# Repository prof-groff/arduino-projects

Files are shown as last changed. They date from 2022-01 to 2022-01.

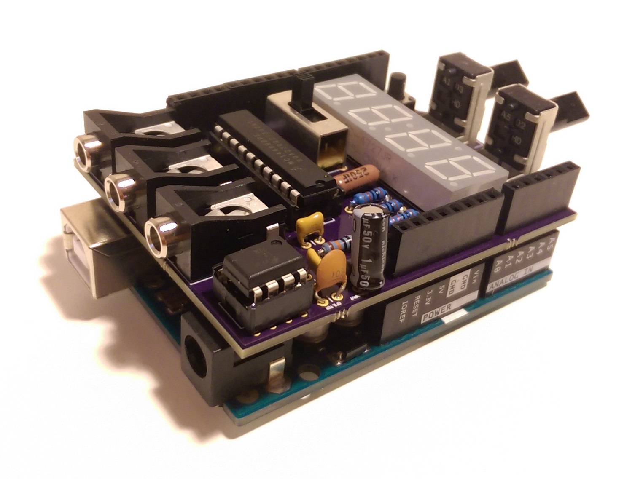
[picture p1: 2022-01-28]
WaveformsIO/img/AssembledBoard.jpg

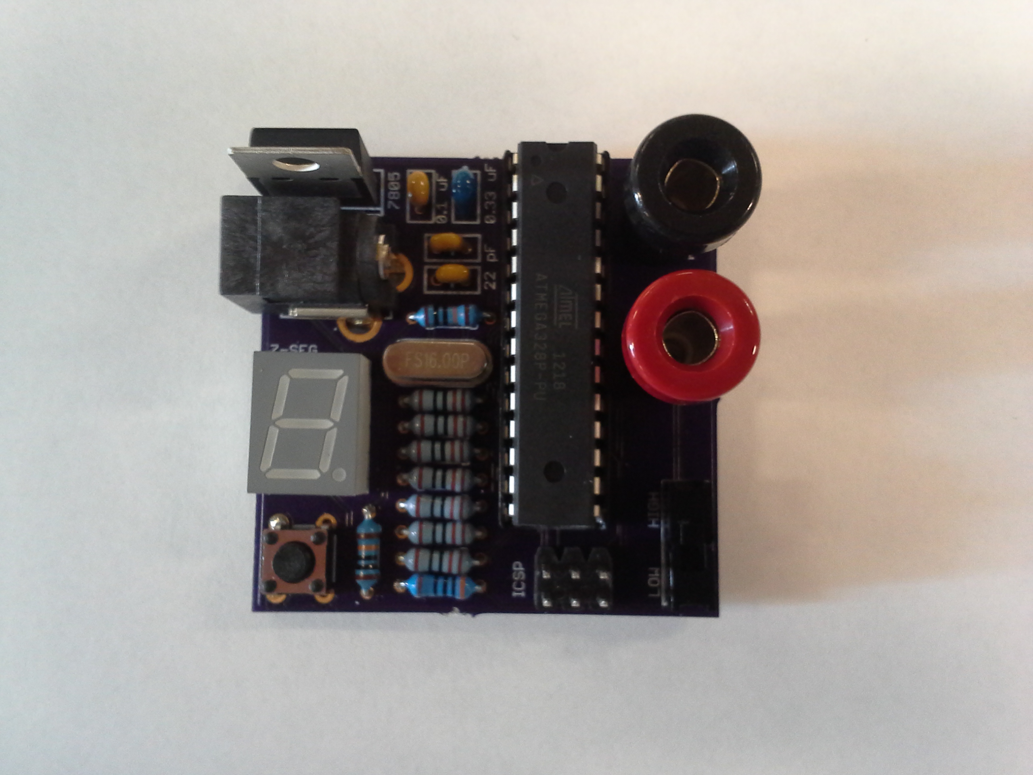
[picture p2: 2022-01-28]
makeToneBoard/img/toneMaker_assembled.jpg

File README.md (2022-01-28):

# arduino-projects

### makeToneBoard Parts List

* 1 x 28-pin DIP Atmel ATmega328p Microcontroller
* 1 x 28-pin DIP socket
* 1 x 7805 5-V linear voltage regulator
* 1 x Lite-On 4301-package 7-segment display
* 1 x 16 MHz Crystal
* 1 x SPST tactile switch/button, normally open, momentarily closed
* 1 x SPDT slide switch
* 1 x 2 rows, 6 positions header
* 1 x female 2.1 mm barrel jack
* 1 x black female banana plug jack
* 1 x red female banana plug jack
* 1 x 300 ohm resistor, 0.25W
* 7 x 110 ohm resistor, 0.25W
* 2 x 100 kohm resistor, 0.25W
* 2 x 22 pF ceramic capacitor, 100V
* 1 x 0.1 microF ceramic capacitor, 50V
* 1 x 0.33 microF ceramic capacitor, 50V

### WaveFormIO Parts List

* Motorola/Freescale MC14489B
* Lite-On LTC-4727JR 4-Digit Display
* ATmega 328P-PU
* 7805
* PTV09A-2020F-A502 Bourns 5k Poteniometer
* PTV09A-2020F-A103 Bourns 10k Poteniometer
* Push Button - Momentary On - Schurter 1301.9305
* E-Switch EG2301A (6mm-tall switch arm)
* 108-0903-001 (Black)
* 108-0902-001 (Red)
* Op-Amp for voltage follower
* TE Connectivity 1-971111-3 Flat Cable 10C 28AWG
* 3365/10-CUT-LENGTH 3M
* OMRON XG4M-1030-T Cable Crip Connector Female
* OMRON XG4C-1031 PCB Socket Male

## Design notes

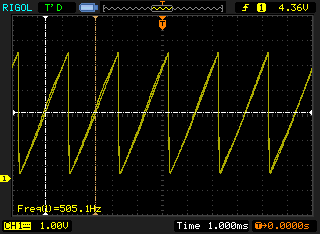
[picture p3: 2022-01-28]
WaveformsIO/img/sawtoothWave.bmp

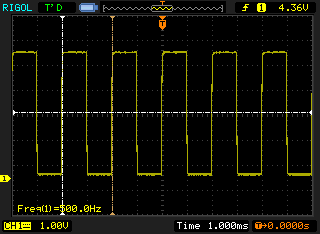
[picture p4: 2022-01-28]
WaveformsIO/img/squareWave.bmp

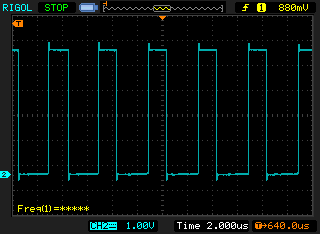
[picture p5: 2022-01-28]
WaveformsIO/img/PWM1.bmp

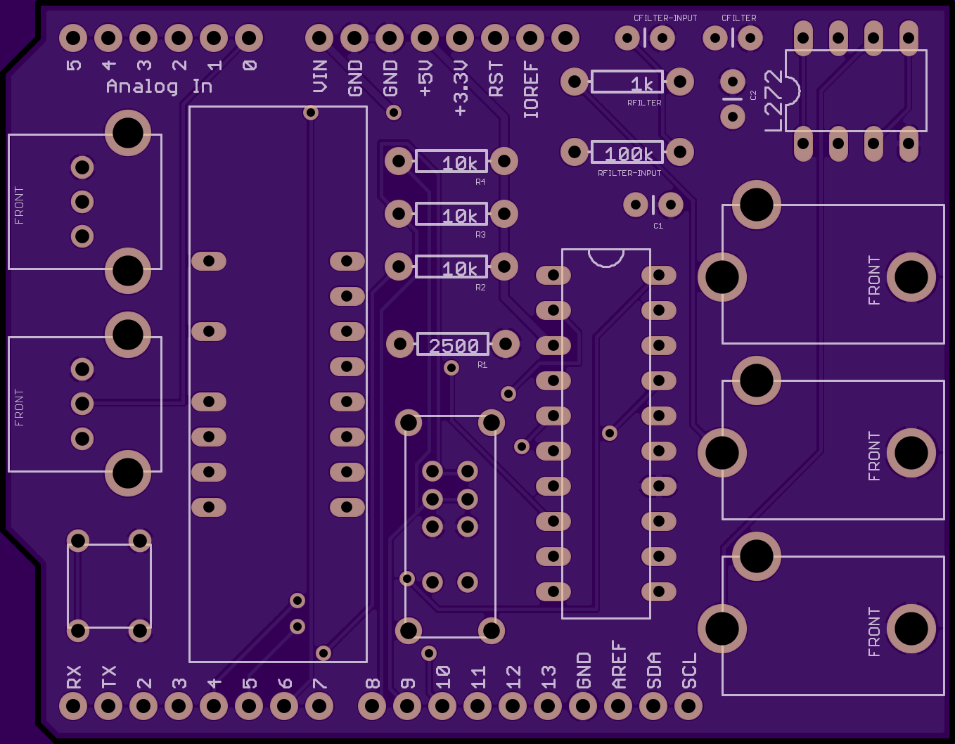
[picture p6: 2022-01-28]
WaveformsIO/img/OSHParkBoard.png

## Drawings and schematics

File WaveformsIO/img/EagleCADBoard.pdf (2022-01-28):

# Analog In RXTX

## CFILTER L272 CFILTER-INPUT C² C1

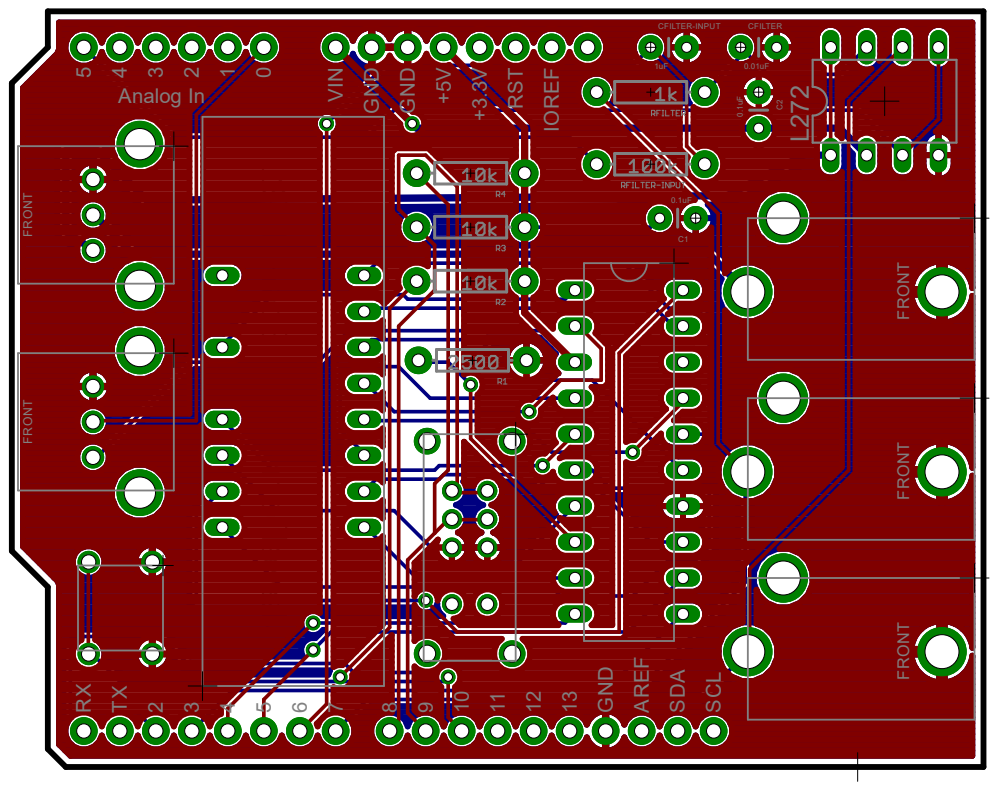
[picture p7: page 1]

910111213GND AREF SDA SCL IOREF FRONT FRONT FRONT FRONT FRONT

GND GND +5V RST VIN +3.3V5

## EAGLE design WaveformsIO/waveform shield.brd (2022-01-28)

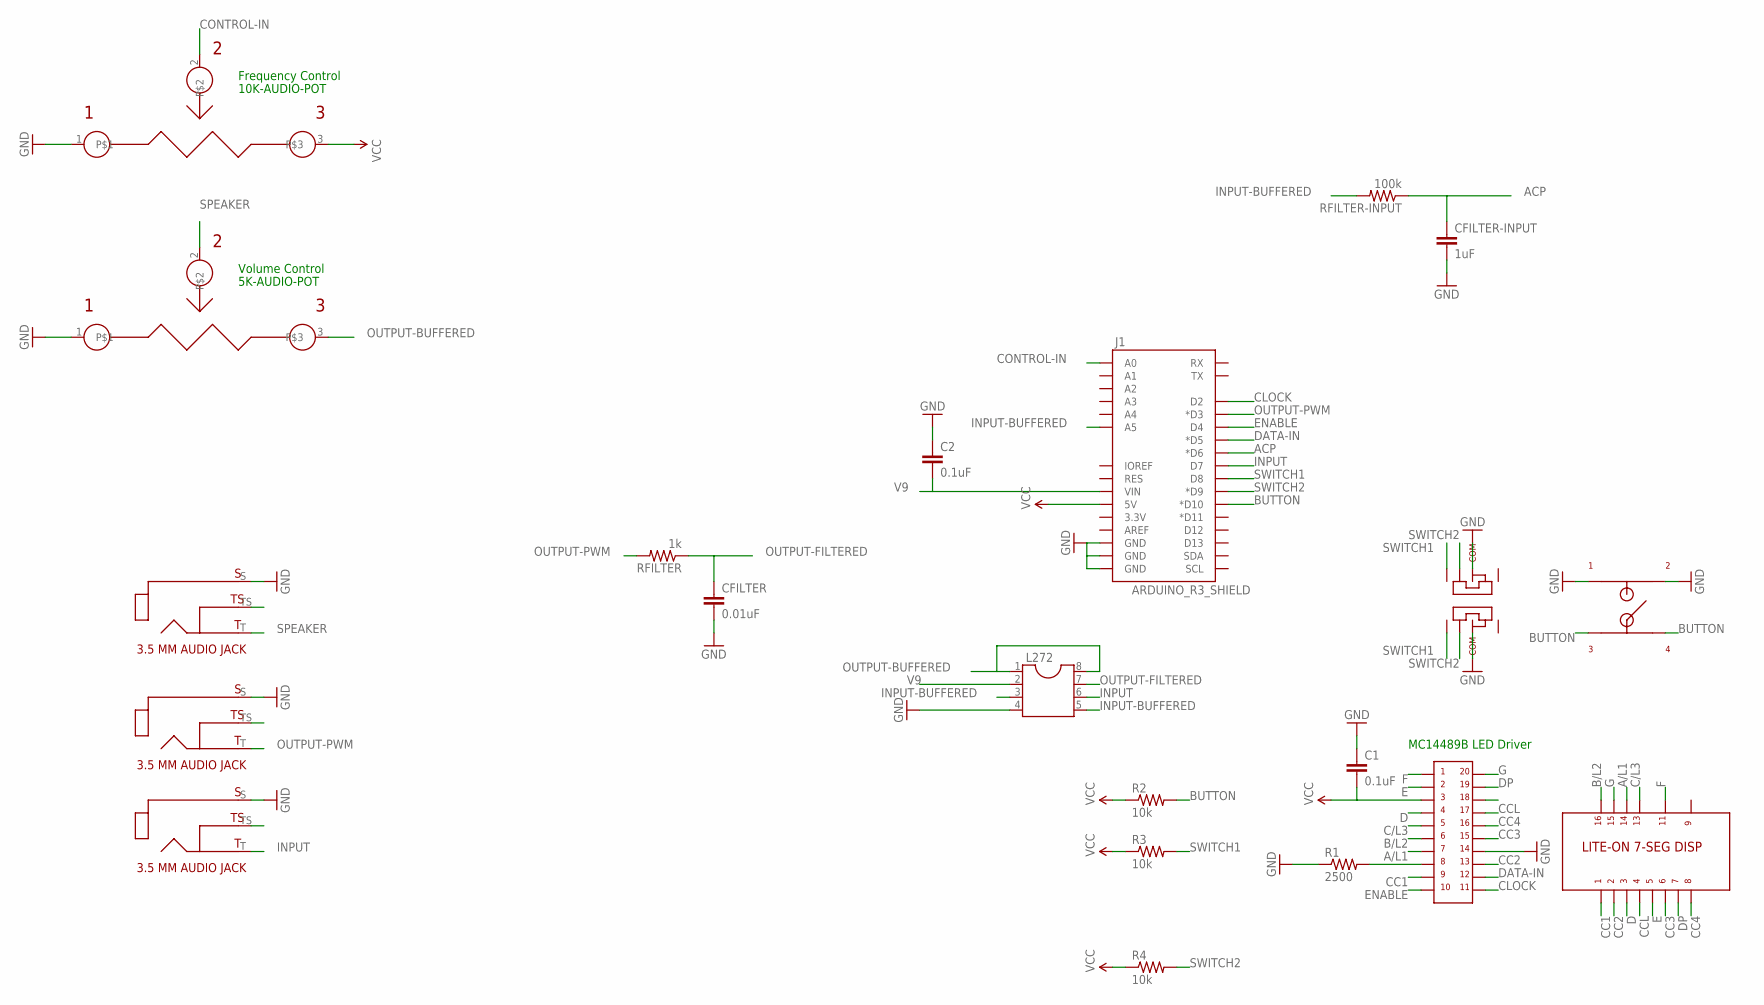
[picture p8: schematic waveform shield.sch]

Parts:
5K-AUDIO-POT: BOURNS-PTV09A-2; BOURNS-POT-PTV09A-2
C1, C2: 0.1uF; CAP-PTH-SMALL
CFILTER: 0.01uF; CAP-PTH-SMALL
CFILTER-INPUT: 1uF; CAP-PTH-SMALL
J1: ARDUINO_R3_SHIELD; UNO_R3_SHIELD
L272: DIL8; DIL08
R1: 2500; AXIAL-0.3
R2, R3, R4: 10k; AXIAL-0.3
RFILTER: 1k; AXIAL-0.3
RFILTER-INPUT: 100k; AXIAL-0.3
U$1: LITE-ON-7-SEG-DISP; 7-SEG-DISPLAY-LITE-ON
U$2: MC14489B-LED-DRIVER; DIP-20
U$3, U$6, U$7: 3.5MM-AUDIO-JACK-CUI; 3.5MM-AUDIO-JACK-MONO-CUI
U$4: E-SWITCH-THREE-WAY-SWITCH; EG2301-SLIDE-SWITCH
U$5: SWITCH-MOMENTARY-ON-SCHURTER
U$9: BOURNS-PTV09A-2; BOURNS-POT-PTV09A-2

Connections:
A/L1: U$1.P$14, U$2.P$7
ACP: CFILTER-INPUT.1, J1.D6 (*D6), RFILTER-INPUT.P$1 (1)
B/L2: U$1.P$16, U$2.P$6
BUTTON: J1.D10 (*D10), R2.P$2 (2), U$5.P$3, U$5.P$4
C/L3: U$1.P$13, U$2.P$5
CC1: U$1.P$1, U$2.P$9
CC2: U$1.P$2, U$2.P$13
CC3: U$1.P$6, U$2.P$15
CC4: U$1.P$8, U$2.P$16
CCL: U$1.P$4, U$2.P$17
CLOCK: J1.D2, U$2.P$11
CONTROL-IN: J1.A0, U$9.2
D: U$1.P$3, U$2.P$4
DATA-IN: J1.D5 (*D5), U$2.P$12
DP: U$1.P$7, U$2.P$19
E: U$1.P$5, U$2.P$2
ENABLE: J1.D4, U$2.P$10
F: U$1.P$11, U$2.P$1
G: U$1.P$15, U$2.P$20
GND: 5K-AUDIO-POT.1, C1.1, C2.1, CFILTER.2, CFILTER-INPUT.2, J1.GND@0 (GND), J1.GND@1 (GND), J1.GND@2 (GND), L272.4, R1.P$1 (1), U$2.P$14, U$3.S, U$4.P$3, U$4.P$7, U$5.P$1, U$5.P$2, U$6.S, U$7.S, U$9.1
INPUT: J1.D7, L272.6, U$7.T
INPUT-BUFFERED: J1.A5, L272.3, L272.5, RFILTER-INPUT.P$2 (2)
unnamed: R1.P$2 (2), U$2.P$8
OUTPUT-BUFFERED: 5K-AUDIO-POT.3, L272.1, L272.8
OUTPUT-FILTERED: CFILTER.1, L272.7, RFILTER.P$1 (1)
OUTPUT-PWM: J1.D3 (*D3), RFILTER.P$2 (2), U$6.T
SPEAKER: 5K-AUDIO-POT.2, U$3.T
SWITCH1: J1.D8, R3.P$2 (2), U$4.P$1, U$4.P$5
SWITCH2: J1.D9 (*D9), R4.P$2 (2), U$4.P$2, U$4.P$6
V9: C2.2, J1.VIN, L272.2
VCC: C1.2, J1.5V, R2.P$1 (1), R3.P$1 (1), R4.P$1 (1), U$2.P$3, U$9.3

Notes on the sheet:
MC14489B LED Driver
5K-AUDIO-POT
10K-AUDIO-POT
Volume Control
Frequency Control

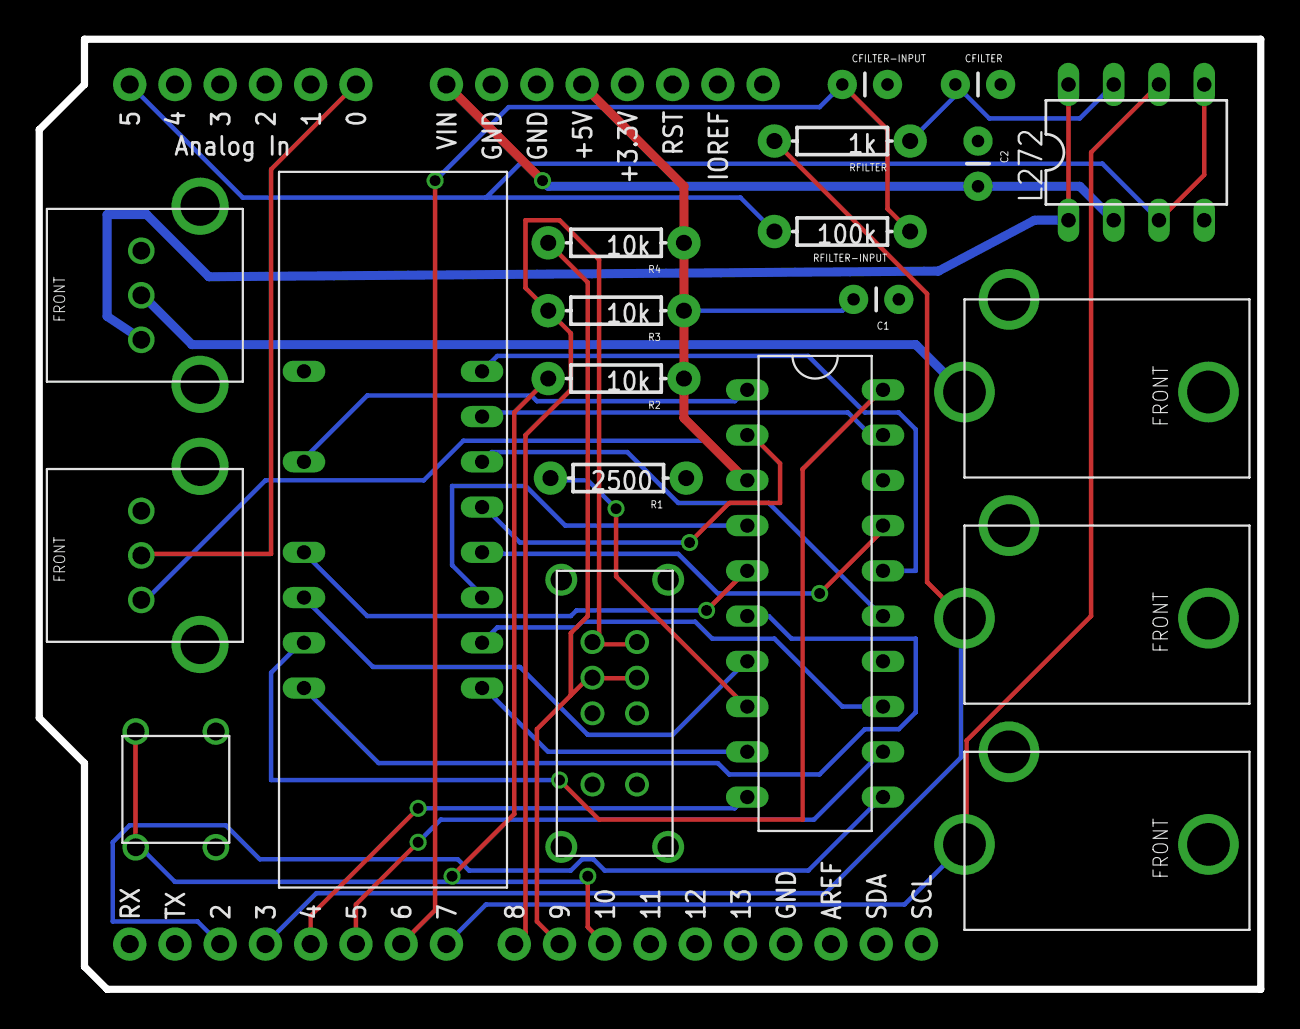
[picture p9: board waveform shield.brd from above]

Board: 2 copper layers, 68.6 x 53.3 mm, 21 parts (0 on the bottom side), 31 nets.

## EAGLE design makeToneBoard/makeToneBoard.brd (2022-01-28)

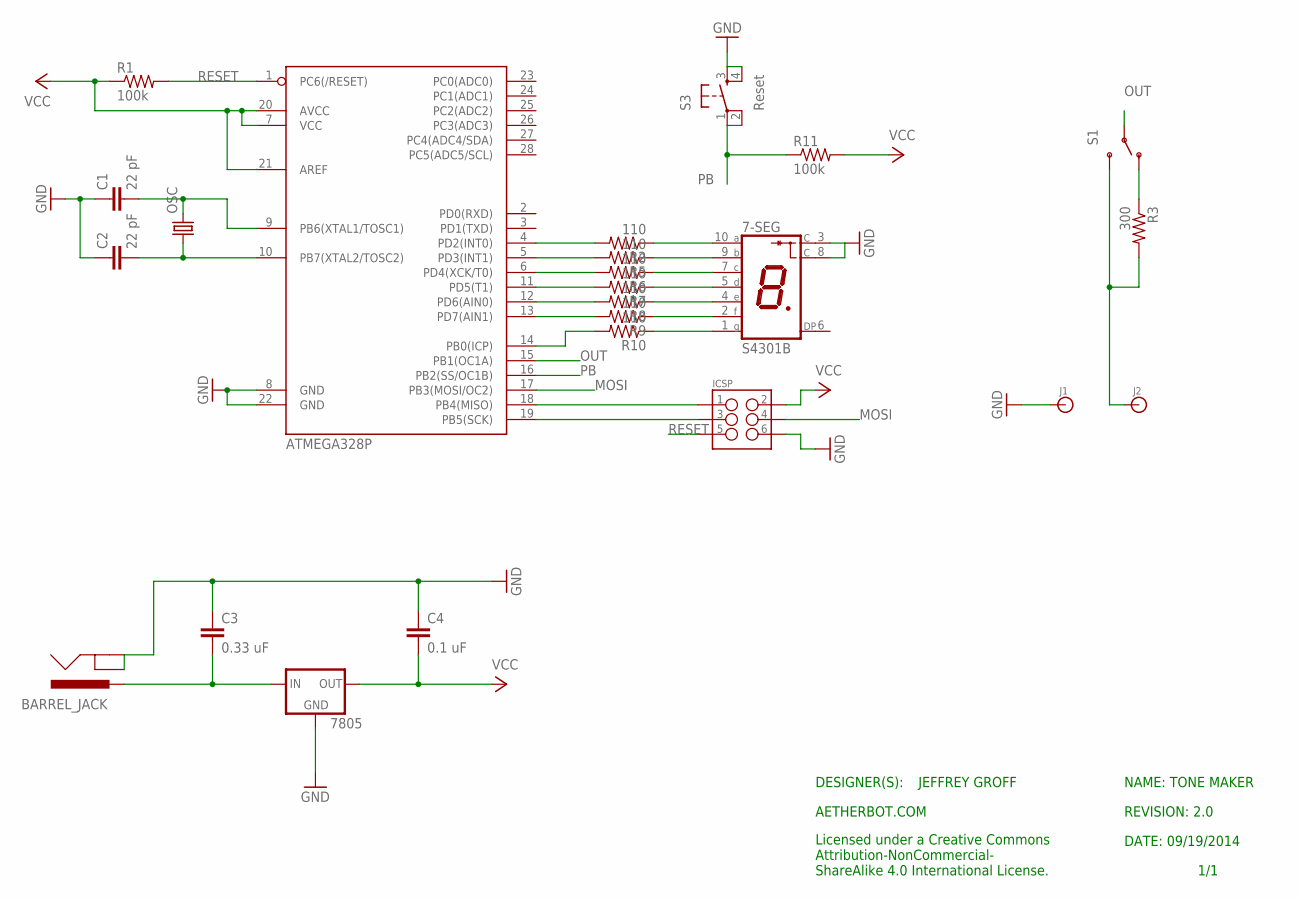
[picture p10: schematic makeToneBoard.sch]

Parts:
7-SEG: S4301B
7805: V_REG_78XXSINK; TO220-IGO
BARREL_JACK: POWER_JACKPTH; POWER_JACK_PTH
C1, C2: 22 pF; CAP-PTH-SMALL-KIT
C3: 0.33 uF; CAP-PTH-SMALLEZ
C4: 0.1 uF; CAP-PTH-SMALLEZ
ICSP: M03X2NO_SILK; 2X3-NS
J1, J2: BANANA_CONN
OSC: CRYSTALHC49S; HC49/S
R1, R11: 100k; 0204/7
R2, R5, R6, R7, R8, R9, R10: 110; 0204/7
R3: 300; 0204/7
S1: LED PWR; SWITCH-SPDT
S3: Reset; TACTILE-PTH
U1: ATMEGA328P; DIL28-3

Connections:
GND: 7-SEG.3 (C), 7-SEG.8 (C), 7805.GND, BARREL_JACK.GND, BARREL_JACK.GNDBREAK, C1.1, C2.1, C3.1, C4.1, ICSP.6, J1.P$1, S3.3, S3.4, U1.8 (GND), U1.22 (GND)
MOSI: ICSP.4, U1.17 (PB3(MOSI/OC2))
unnamed: R2.2, U1.4 (PD2(INT0))
unnamed: R3.1, S1.1 (O)
unnamed: J2.P$1, R3.2, S1.3 (S)
unnamed: 7-SEG.1 (G), R10.1
unnamed: C2.2, OSC.1, U1.10 (PB7(XTAL2/TOSC2))
unnamed: 7-SEG.10 (A), R2.1
unnamed: R5.2, U1.5 (PD3(INT1))
unnamed: 7-SEG.9 (B), R5.1
unnamed: R6.2, U1.6 (PD4(XCK/T0))
unnamed: 7805.IN, BARREL_JACK.PWR, C3.2
unnamed: 7-SEG.7 (C), R6.1
unnamed: R7.2, U1.11 (PD5(T1))
unnamed: 7-SEG.5 (D), R7.1
unnamed: ICSP.1, U1.18 (PB4(MISO))
unnamed: ICSP.3, U1.19 (PB5(SCK))
unnamed: R8.2, U1.12 (PD6(AIN0))
unnamed: 7-SEG.4 (E), R8.1
unnamed: R9.2, U1.13 (PD7(AIN1))
unnamed: 7-SEG.2 (F), R9.1
unnamed: R10.2, U1.14 (PB0(ICP))
unnamed: C1.2, OSC.2, U1.9 (PB6(XTAL1/TOSC1))
OUT: S1.2, U1.15 (PB1(OC1A))
PB: R11.1, S3.1, S3.2, U1.16 (PB2(SS/OC1B))
RESET: ICSP.5, R1.2, U1.1 (PC6(/RESET))
VCC: 7805.OUT, C4.2, ICSP.2, R1.1, R11.2, U1.7 (VCC), U1.20 (AVCC), U1.21 (AREF)

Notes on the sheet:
NAME: TONE MAKER
JEFFREY GROFF
DATE: 09/19/2014
DESIGNER(S):
1/1
REVISION: 2.0
AETHERBOT.COM
Licensed under a Creative Commons Attribution-NonCommercial- ShareAlike 4.0 International License.

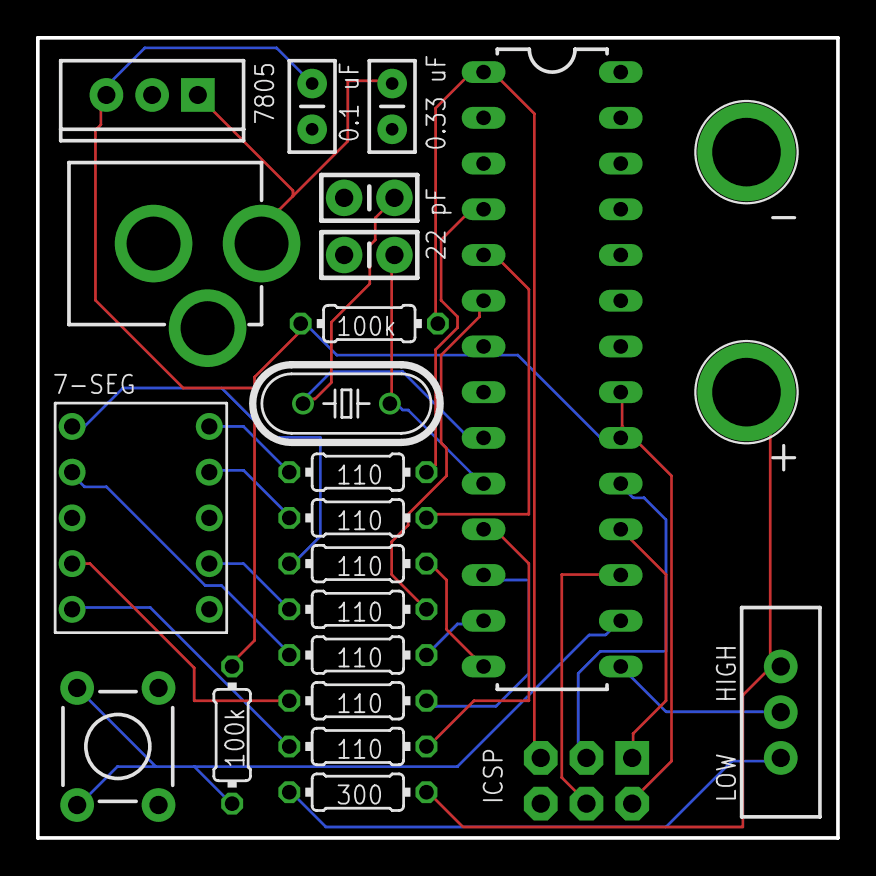
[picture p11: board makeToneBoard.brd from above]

Board: 2 copper layers, 44.5 x 44.5 mm, 24 parts (0 on the bottom side), 27 nets.

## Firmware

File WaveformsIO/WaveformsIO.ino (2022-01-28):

#include "WaveformsIO.h"

// Enable Pin, Data Pin, Clock Pin, Switch Pin 1, Switch Pin 2, and Button Pin are 
// 4, 5, 2, 8, 9, and 10, respectively
WaveformsIO myWave(4, 5, 2, 8, 9, 10);

// float myNum = 0;
// byte cur_waveform[64];
// byte wave_shape = 1;

// byte PBREG;

// C4 through C5
const float scale[8] = {261.626, 293.665, 329.628, 349.228, 391.995, 440, 493.883, 523.251};

// define waveforms
// sawtooth wave
const byte sawtooth[64] = {0,1,2,3,4,5,6,7,8,9,10,11,12,13,14,15,16,17,18,19,20,21,22,23,24,25,26,27,28,29,30,31,32,33,34,35,36,37,38,39,40,41,42,43,44,45,46,47,48,49,50,51,52,53,54,55,56,57,58,59,60,61,62,63};
// triangle wave
const byte triangle[64] = {0,2,4,6,8,10,12,14,16,18,20,22,24,26,28,30,32,33,35,37,39,41,43,45,47,49,51,53,55,57,59,61,63,61,59,57,55,53,51,49,47,45,43,41,39,37,35,33,32,30,28,26,24,22,20,18,16,14,12,10,8,6,4,2};
// sine wave
const byte sine[64] = {32,35,38,41,44,46,49,51,54,56,58,59,61,62,62,63,63,63,62,62,61,59,58,56,54,51,49,46,44,41,38,35,32,28,25,22,19,17,14,12,9,7,5,4,2,1,1,0,0,0,1,1,2,4,5,7,9,12,14,17,19,22,25,28};
// square wave
const byte squarewave[64] = {0,0,0,0,0,0,0,0,0,0,0,0,0,0,0,0,0,0,0,0,0,0,0,0,0,0,0,0,0,0,0,0,63,63,63,63,63,63,63,63,63,63,63,63,63,63,63,63,63,63,63,63,63,63,63,63,63,63,63,63,63,63,63,63};

byte waveform[64];

volatile byte iSample = 0;
const byte nSamples = 64; // selected to balance sampling resolution with range of attanable frequencies

byte shape = 2;
float frequency;



// stuff for frequency measuring
// This code measure the frequency of an incoming periodic signal using Timer1 and the
// onboard comparator. For squrewaves the code should work regardless of the duty-cycle.
volatile unsigned int overflows = 0;
volatile unsigned long edges = 0;
volatile unsigned long tstart = 0;
volatile unsigned long tstop = 0;
volatile unsigned long tnow = 0;
const unsigned long cycles = 100; // how many cycles to average over

float frequencyIn; 

int potCur, potLast;

int maxFrequency = 1000;

void setup() {
  myWave.ConfigureDisplay(false, true);
  Serial.begin(9600);
  potCur = analogRead(0);
  potLast = potCur;
  frequency = ((float)potCur/1023)*maxFrequency;

  pinMode(3, OUTPUT);  


  //  myWave.GetMode();
  //  SelectWaveform(myWave.mode);
  //  GenerateWaveform(frequency);
  //  myWave.WriteToDisplay(frequency);
  SelectWaveform(shape);
  GenerateWaveform(frequency);
  myWave.WriteToDisplay(frequency);
  delay(500);
  
}

void loop() {
//  // three modes controlled by switch: function generator, tone generator, and frequency measurer
//  // as function generator: button changes waveform shape while two potentiometers change frequency and volume
//  // as tone generator: button changes note (sine wave) while one potentiometers changes volume
//  // as frequency measurer: button and potentiometers are disabled. 


while(1) {
  if(digitalRead(10)==LOW) {
    // Serial.println("hi");
    shape++;
    if (shape > 4) {
      shape = 1;
    }
    SelectWaveform(shape);
    GenerateWaveform(frequency);
    myWave.WriteToDisplay(frequency);
    delay(500);
  }
  
  potCur = analogRead(0);
  if (abs(potCur - potLast)>5) {
    frequency = ((float)potCur/1023)*maxFrequency;
    GenerateWaveform(frequency); 
    myWave.WriteToDisplay(frequency);
    potLast = potCur;
    delay(100);
  }
}

while(0) {
  frequency = 0;
  for(byte i = 0; i < 100; i++) {
    frequency = frequency + analogRead(0);
  }
  frequency = ((frequency/1023)/100)*1000;
  GenerateWaveform(frequency);
  myWave.WriteToDisplay(frequency);
  delay(100);
}

//if(myWave.GetMode()) {
//  InitializeWaveform(myWave.mode);
//  GenerateWaveform(frequency);
//  myWave.WriteToDisplay(frequency);
//}
   
//  while (myWave.mode == 1) { // mode 1
//    // do function generator
//    myWave.WriteToDisplay(1);
//    
//    
//    if(myWave.GetMode()) {
//      break;
//    }
//  }
//  
//  while (myWave.mode == 2) { // mode 2
//    // do tone generator
//    myWave.WriteToDisplay(2);
//    
//    if(myWave.GetMode()) {
//      break;
//    }
//  }
//  
//  while (myWave.mode == 3) { // mode 3
//    // do frequency measurer
//    myWave.WriteToDisplay(3);
//    
//    if(myWave.GetMode()) {
//      break;
//    }
//  }

}



void SelectWaveform(byte shape) {


  if (shape == 1) {
    for (int i = 0; i < nSamples; i++) {
      waveform[i] = squarewave[i];
    }
    
  }
  else if (shape == 2) {
    for (int i = 0; i < nSamples; i++) {
      waveform[i] = sine[i];
    }
  }
  else if (shape == 3) {
    for (int i = 0; i < nSamples; i++) {
      waveform[i] = triangle[i];
    }
  }
  else if (shape == 4) {
    for (int i = 0; i < nSamples; i++) {
      waveform[i] = sawtooth[i];
    }
  }
  else {
    // error
  }
}

void GenerateWaveform(float frequency) {

    // set up timer/counter 2, fast PWM with OCR2A as TOP, OC2B (pin 5, DP3) set high at BOTTOM and set LOW on output on compare match with OCR2B (non-inverting mode)
    TCCR2A = B00100011;
    TCCR2B = B00001001; // no prescaler (bit 0)
    OCR2A = 63; // OCR2A is one byte, smaller values increase frequency of PWM output on OC2B
    OCR2B = waveform[iSample];
    TIMSK2 = B00000000;
    
    // set up timer/counter 1, normal mode, no output, fast PWM, OCR1A is TOP, no prescaler
    TCCR1A = B00000011; 
    TCCR1B = B00011001;
  
    TIMSK1 = B00000010; // enable interrupt when OCR1A is reached
    
    // timer/counter 1 sets the rate at which the sample value is changed and, thus, the frequency of the output waveform.
    OCR1A = round(16e6/(nSamples*frequency)) - 1;

}

ISR(TIMER1_COMPA_vect) {
  iSample++;
  if (iSample == nSamples) {
    iSample = 0;
  }
  OCR2B = waveform[iSample];
}



void measureFreq() {
  edges = 0;
  // ACSR = ACSR | B01000100; // comparator input capture enabled using internal bandgap voltage on positive input 
 
  ACSR = ACSR | B00000010; // enable analog comparator interrupt (bit 3) on failing edge (bit 1) 
  // using external reference voltage on digital pin 6 (AIN0) (bit 6 = 0)  
  
  overflows = 0;
  
  TCCR1A = B00000000; // set timer/counter 1 in normal mode where it will count to 0xFFFF then repeat
  TCCR1B = B10000000; // input capture enabled with capture on falling edge (bit 6 = 0) which would
  // correspond to a rising edge of the actual signal being detected. bit 7 = 1 turns on the noise canceler
  TIMSK1 = TIMSK1 | B00000001; // enables Timer1 input capture interrupt (bit 5) and/or overflow interrupt (bit 0)
  
  // turn on the counter - no prescaler
  TCCR1B = TCCR1B | B00000001;
  ACSR = ACSR | B00001000; // enable analog comparator interrupt (bit 3)
  
  while (edges < (cycles+1)) {
    // do nothing
  }
  
  // calculate the frequency 
  frequencyIn = (float)16000000*(float)cycles/(float)(tstop - tstart);
  
  
  
}


ISR(TIMER1_OVF_vect) {
  overflows += 1;
  }
 
 
  ISR(ANALOG_COMP_vect)
  {
    tnow = TCNT1;
    edges += 1;
    if (edges == 1) {
     tstart = overflows*65536 + tnow;
    }
   else if (edges == cycles + 1) {
     tstop = overflows*65536 + tnow;
     // turn off the clock and comparator
     ACSR = 0;
     TCCR1B = 0;
   }
  }

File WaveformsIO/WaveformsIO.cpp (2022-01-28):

#include "WaveformsIO.h"
#include <Arduino.h>

WaveformsIO::WaveformsIO(byte EP, byte DP, byte CP, byte S1P, byte S2P, byte BP) { 
  m_EP = EP;
  m_DP = DP;
  m_CP = CP; 
  
//  byte S1P = 8;
//  byte S2P = 9;
//  byte BP = 10;
//  // S1P, S2P, and BP are pins 8, 9, and 10, which are bits 0, 1, and 2 respectively in PORTB
//  // set these pins as inputs
//  
  m_S1P = S1P;
  m_S2P = S2P;
  m_BP = BP;
  
  pinMode(m_S1P, INPUT);
  pinMode(m_S2P, INPUT);
  pinMode(m_BP, INPUT);
  
  pinMode(m_EP, OUTPUT);
  digitalWrite(m_EP, HIGH);
  pinMode(m_DP, OUTPUT);
  digitalWrite(m_CP, LOW);
  pinMode(m_CP, OUTPUT);
  digitalWrite(m_CP, LOW);
  
  updateCR = true;
  
  mode = 0;
  GetMode();
  
  CR = B11000000;
  DR = 0x00000000; // only needs to be 24-bits so two most significant hex digits are unused

}
	
void WaveformsIO::ConfigureDisplay(boolean blank, boolean dim) {
  m_blank = blank;
  m_dim = dim;
  
  CR_last = CR;
  
  if (m_blank) {
    CR = CR & B11111110;
  }
  else {
    CR = CR | B00000001;
  }
  
  if (CR != CR_last) { 
    updateCR = true;
  }
  
  
  if (m_dim) {
    DR = DR & 0b11111111011111111111111111111111;
  }
  else {
    DR = DR | 0b00000000100000000000000000000000;
  }
  
}
  
void WaveformsIO::WriteToDisplay(float num) {
  if (num > 9999) {
    NumberOverflow();
  }
  else {
    CR_last = CR;
    CR = CR | B00100000; // needed to disable bank 5 (semi-colon and high dot)
    if (CR != CR_last) {
      updateCR = true;
    }
    	
    DR = DR & 0b11111111100000000000000000000000; // reset bits that set digits in banks 1-4 (with bank 5 blank, set to show 0) and decimal place location
    
    // determine location of decimal place
    if (num >= 1000) {
      digits = round(num);
      DR += 0x00400000; // 0b00000000010000000000000000000000, ones (bank 4)
    }
    else if (num >= 100) {
      digits = round(num*10);
      DR += 0x00300000; // 0b00000000001100000000000000000000, tenths (bank 3)
    }
    else if (num >= 10) {
      digits = round(num*100);
      DR += 0x00200000; // 0b00000000001000000000000000000000, hundredths (bank 2)
    }
    else {
      digits = round(num*1000);
      DR += 0x00100000; // 0b00000000000100000000000000000000, thousandths (bank 1)
    }
    
    // find digits to display
    d1 = digits/1000;
    d2 = (digits/100) % 10;
    d3 = (digits/10) % 10;
    d4 = digits % 10;
    
    DR = DR + d1 + 0x00000010*d2 + 0x00000100*d3 + 0x00001000*d4;
    // digit place numbering is left to right; e.g, d1 is the thousands place but is the least significant element of the hex code; might change on hardware revision
  }
  
  if (updateCR) {
    digitalWrite(m_EP, LOW);
    for (byte ii=0; ii<8; ii++) {
      if (CR & (B10000000 >> ii)) {
        digitalWrite(m_DP, HIGH);
      }
      else {
        digitalWrite(m_DP, LOW);
      }
      digitalWrite(m_CP, HIGH);
      digitalWrite(m_CP, LOW);
    }
    digitalWrite(m_EP, HIGH);
    updateCR = false;
  }
  digitalWrite(m_EP, LOW);
  for (byte ii=0; ii<24; ii++) {
    if (DR & (0x00800000 >> ii)) {
      digitalWrite(m_DP, HIGH);
    }
    else {
      digitalWrite(m_DP, LOW);
    }
    digitalWrite(m_CP, HIGH);
    digitalWrite(m_CP, LOW);
  }
  digitalWrite(m_EP, HIGH);

}

void WaveformsIO::NumberOverflow() {
  CR_last = CR;
  CR = CR | B00110010;
  if (CR != CR_last) { 
    updateCR = true;
  }
  DR = DR & 0b11111111100000000000000000000000;
  DR += 0x00005F00; // 0b00000000000000000101111100000000;
}	

boolean WaveformsIO::GetMode() {
  byte currentMode = mode;
  boolean modeChange = false;
  
  if (digitalRead(m_S1P)==LOW) {
    mode = 1;
  }
  else if (digitalRead(m_S2P)==LOW) {
    mode = 2;
  }
  else {
    mode = 3;
  }
 
  
  if (currentMode != mode) {
    modeChange = true;
  }
  return modeChange;
}

    

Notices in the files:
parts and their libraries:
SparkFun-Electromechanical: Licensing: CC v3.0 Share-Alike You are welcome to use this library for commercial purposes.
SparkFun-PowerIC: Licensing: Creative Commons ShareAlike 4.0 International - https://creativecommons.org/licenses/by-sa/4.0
